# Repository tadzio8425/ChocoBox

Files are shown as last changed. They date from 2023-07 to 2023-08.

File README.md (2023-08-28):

<div>
  <h1>     ChocoBox</h1>
</div>

### Environment replicator for cocoa fermentation:
- Electronic system that replicates a real life environment. Includes:
  - Continous environmental humidity and temperature measurement
  - Real-time control of both humidity and temperature
  - Spline generation to emulate environmental changes
  - Intuitive set-up and data collection via .txt files
- Backend developed using the Arduino Framework and an ESP32 development board.
- Frontend mobile app developed using the Expo Framework and React-Native.
- Developed in the *Universidad de Los Andes* for the *Biomicrosystems research group*.

## Developed by: 
<ul>
  <li>Juan Sebastián Ortega (https://github.com/tadzio8425)</li>
  <li>Nicolás Correal (https://github.com/Correaln47)</li>
</ul>

## Quickstart
### 1. Setting-up the files...

#### i. Creating the files
The ChocoBox system uses three *.txt* files inside a **MicroSD Card** in order to function, these files are *environment.txt*, *spline.txt* and *datalog.txt*. Altough these files have the *.txt* format, their content is designed to be read as a *.csv*. For the proper functioning of the system, it is **obligatory** for the files to be named exactly like this. If it is your first time using ChocoBox, or if you are resetting the system, please delete all previous files from the SD Card and create three empty *.txt* files.

<p align="center">
   
</p>
<p align="center">
   <i>a. Contents of the MicroSD Card</i>
</p>

#### ii. Setting-up the environment
The environment to be replicated can be easily set in the *environment.txt* file. In order to to this, simply write the *csv* headers in the first row. These headers should be **hour, temperature, humidity**. Then, following the header order, write the desired values for specific hours in each new line. For example, this file replicates an environment for 96 hours, setting new desired values each 24 hours. There is no inverval restriction, neither there is a necessity for an interval, just make sure that the next hour is always greater than the previous one! **Please make sure that there are no extra new lines or blank spaces!**

<p align="center">
   
</p>
<p align="center">
   <i>b. Example of an environment.txt file</i>
</p>

#### iii. Joining the dots
In order to replicate how these variables behave smoothly in nature, a cubic spline algorithm is used in order to fill the gaps between the dots set in *environment.txt*. The results of this algorithm are saved by the microcontroller in *spline.txt*, so this file must not be modified in any way by the user. If the **reference values** shown by the system are not logical, please check the *spline.txt* file. A *spline.txt* with **Nan** values or other errors indicates that *environment.txt* was wrongly formated! 

<p align="center">
   
</p>
<p align="center">
   <i>c. Example of a correctly generated spline.txt file</i>
</p>

#### iv. Step by step
A fundamental part of the spline algorithm is the **step**, this value determines the interval for intermediate points to be calculated and also for data capture. For example, a step of **30 minutes** will make the system update its reference values and save its environmental data each, well, 30 minutes. The smaller the step, the more data will be captured and the smoother the system will be. **Beware of using extremely small steps, as they may lead to a memory overflow in the ESP32!** The **step can be modified by the user**, this will be explained in a further section.

#### v. Getting the data
All environmental data captured by the sensors is saved in *datalog.txt*, which is automatically updated by the microcontroller. This file includes the sensed information of each individual humidity and temperature sensor, captured each **step**. This file follows the order of the following headers: **time(min), tempA(degC), tempB(degC), tempC(degC), tempD(degC), humidLeft(%), humidRight(%)**

The presence of **Nan** values in this file may indicate a sensor malfunction!

<p align="center">
   
</p>
<p align="center">
   <i>d. Example of a correctly generated datalog.txt file</i>
</p>

## 2. PCB Connections
Handling the PCB should be avoided at all costs. However, in the case that something has gone wrong or a new interface/sensor needs to be added, the following connection diagram should be **strictly** followed. All cables are marked with their respective signal.

| PCB Overview |
| --- |
|   |

| DS18B20 (Temp) | DHT22 (Hum) | MicroSD |
| --- | --- | --- |
||||

| I2C (LCD Screen and Clock) | Humidifier and Heater Relay | 12V and WaterLevel |
| --- | --- | --- |
||||

## 3. Cable management
ChocoBox uses an electric extension to power itself, the extension input should be conected directly to the power socket. This extesion has 3 available output sockets, of which only 2 are actually used. One of the sockets must me connected to the **resistor cable**, which handles the power given to the heating resistors. The second socket must be connected to a **12V-2A** power supply that powers the electronics. The output of the power supply is a **jack connector** which goes directly into the PCB box. Remember that you may find the extension sockets on the floor, behind the resistor wooden holder. Please make sure that all major cables are correctly pluged-in before performing any test, also **do not handle cables under any circumstance unless the resistors are totally cold**.

- To completely **TURN-OFF** the system, you only need to unplug the extension input from the power socket.

## 4. Operating the system
Once everything is pluged-in, the system should start to work autonomously. This means that the desired values from *environment.txt* will be replicated inside the box, following the intermidiate points generated in *spline.txt* and the actual sensed values will be saved each **step** in *datalog.txt*.

### i. Monitoring 01: LCD Screen
The most straigth-forward method to monitor the system is by looking at its **20x4 LCD Screen**. This screen depicts the following data, line by line:
  1. **Humidity**: Displays the current humidity average inside the box in (%).
  2. **Temperature**: Displays the current temperature average inside the box in (°C).
  3. **Ref**: Displays the reference values that the system should be trying to achieve in that specific moment.
  4. **Time**: Displays how much time has the system been on a specific fermentation cycle. This timer **DOES NOT** reset when the system is disconnected, as it is programmed to retake fermentation despite a possible temporal failure. However, it can be reset **manually**.

| LCD Screen |
| --- |
|   |

### ii. Connecting to the ESP32 via WiFi
The ESP32 is set in *AP* mode, which means that it acts as an *Access Point* (A.K.A. its own WiFi network). In order to connect, simply search for the network called **ChocoBox** and establish a connection using the **secret password**. It is **important** that this password is only given to authorized staff, otherwise, a fermentation cycle could be jeopardized.

- **Once connected to the _ChocoBox_ network, the ESP32 can be accessed using its IP Address which will always be:**
- **192.168.1.1**

| The ChocoBox Network |
| --- |
|   |

### iii. Monitoring 02: Rest API

| Root: / |
| --- |
|   |

Accessing the root of the rest API via any browser (192.168.1.1/) displays the current state of its variables. Thus, ChocoBox can be monitored in real time without the need of an external app.

| Request | Path  | Description |
| --- | --- | --- |
| GET | /datalog  | Downloads the dataLog up to the latest measurement.|
| POST | /environment | Uploads an environment.txt to the system. When the system is reset, the uploaded file will set a new curve to follow. The included python script displays its POST format.|
| POST | /step | Updates the step of the spline algorithm. Its content must be a number that represents a certain number of hours (at least 0.05).|

### iv. Monitoring 03: App
An app was developed using the Expo Framework in order to unify all the API Requests in an intuitive and user friendly interface.

| Init Page| Main Page | Data Module |
| --- | --- | --- |
|  |  | |

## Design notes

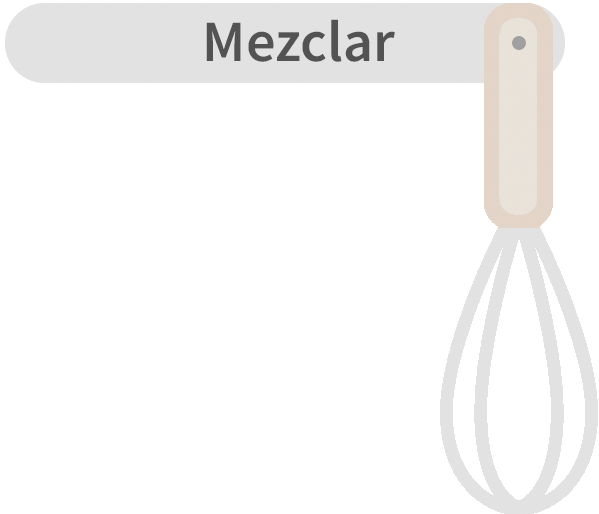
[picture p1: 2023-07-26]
ChocoboxApp/assets/images/batidora_mangotext.png

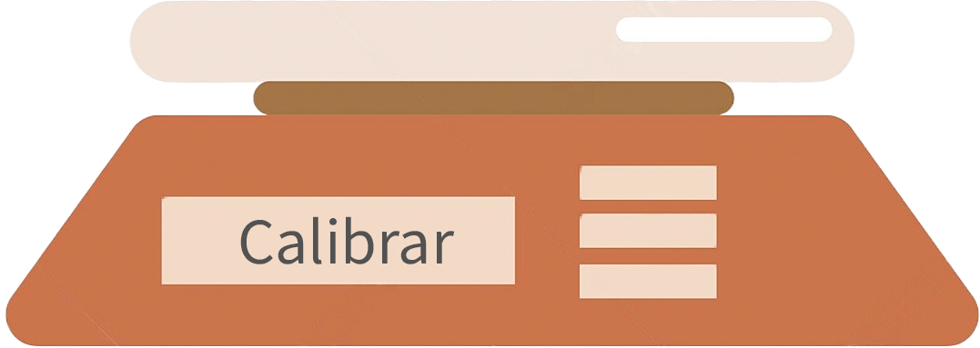
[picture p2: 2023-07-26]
ChocoboxApp/assets/images/balanza.png

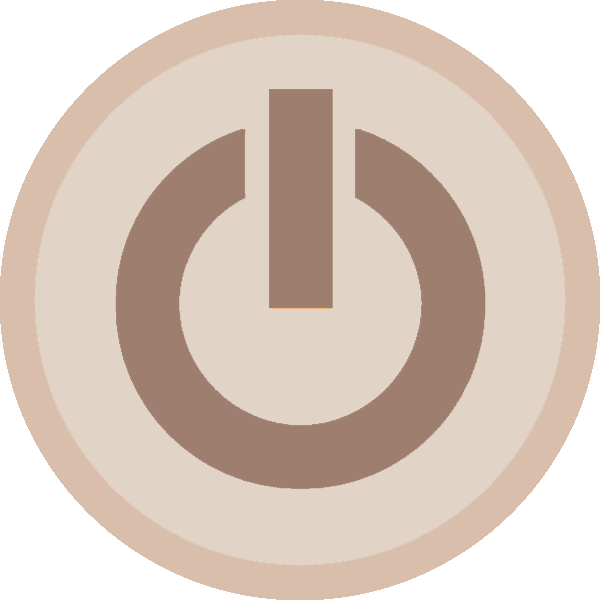
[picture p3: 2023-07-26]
ChocoboxApp/assets/images/offButton.png

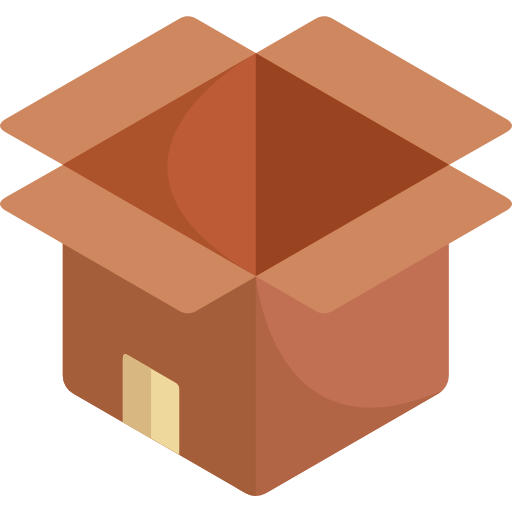
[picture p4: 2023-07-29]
ChocoboxApp/assets/images/package.png

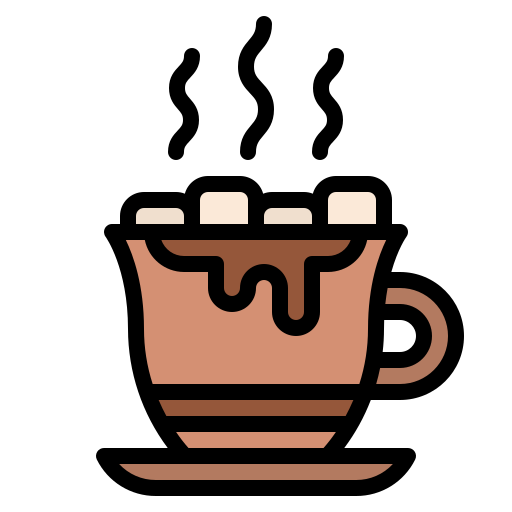
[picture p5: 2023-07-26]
ChocoboxApp/assets/images/hot-chocolate.png

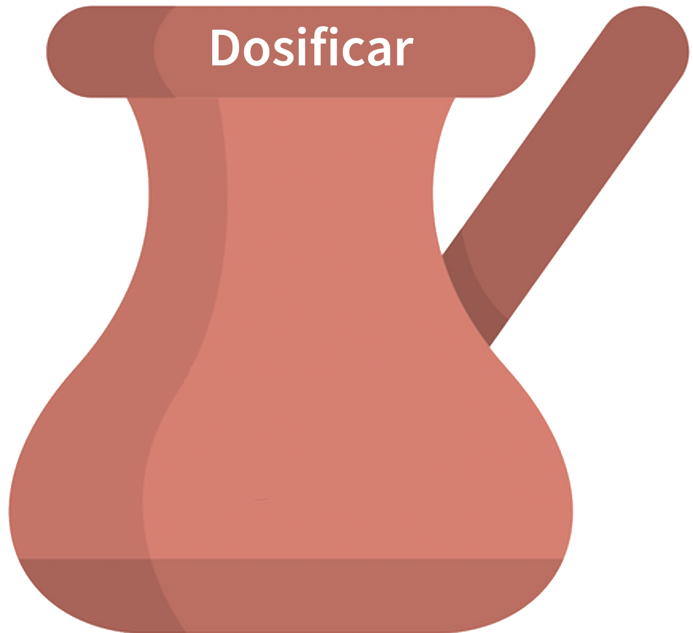
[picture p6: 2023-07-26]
ChocoboxApp/assets/images/chocolatera.png

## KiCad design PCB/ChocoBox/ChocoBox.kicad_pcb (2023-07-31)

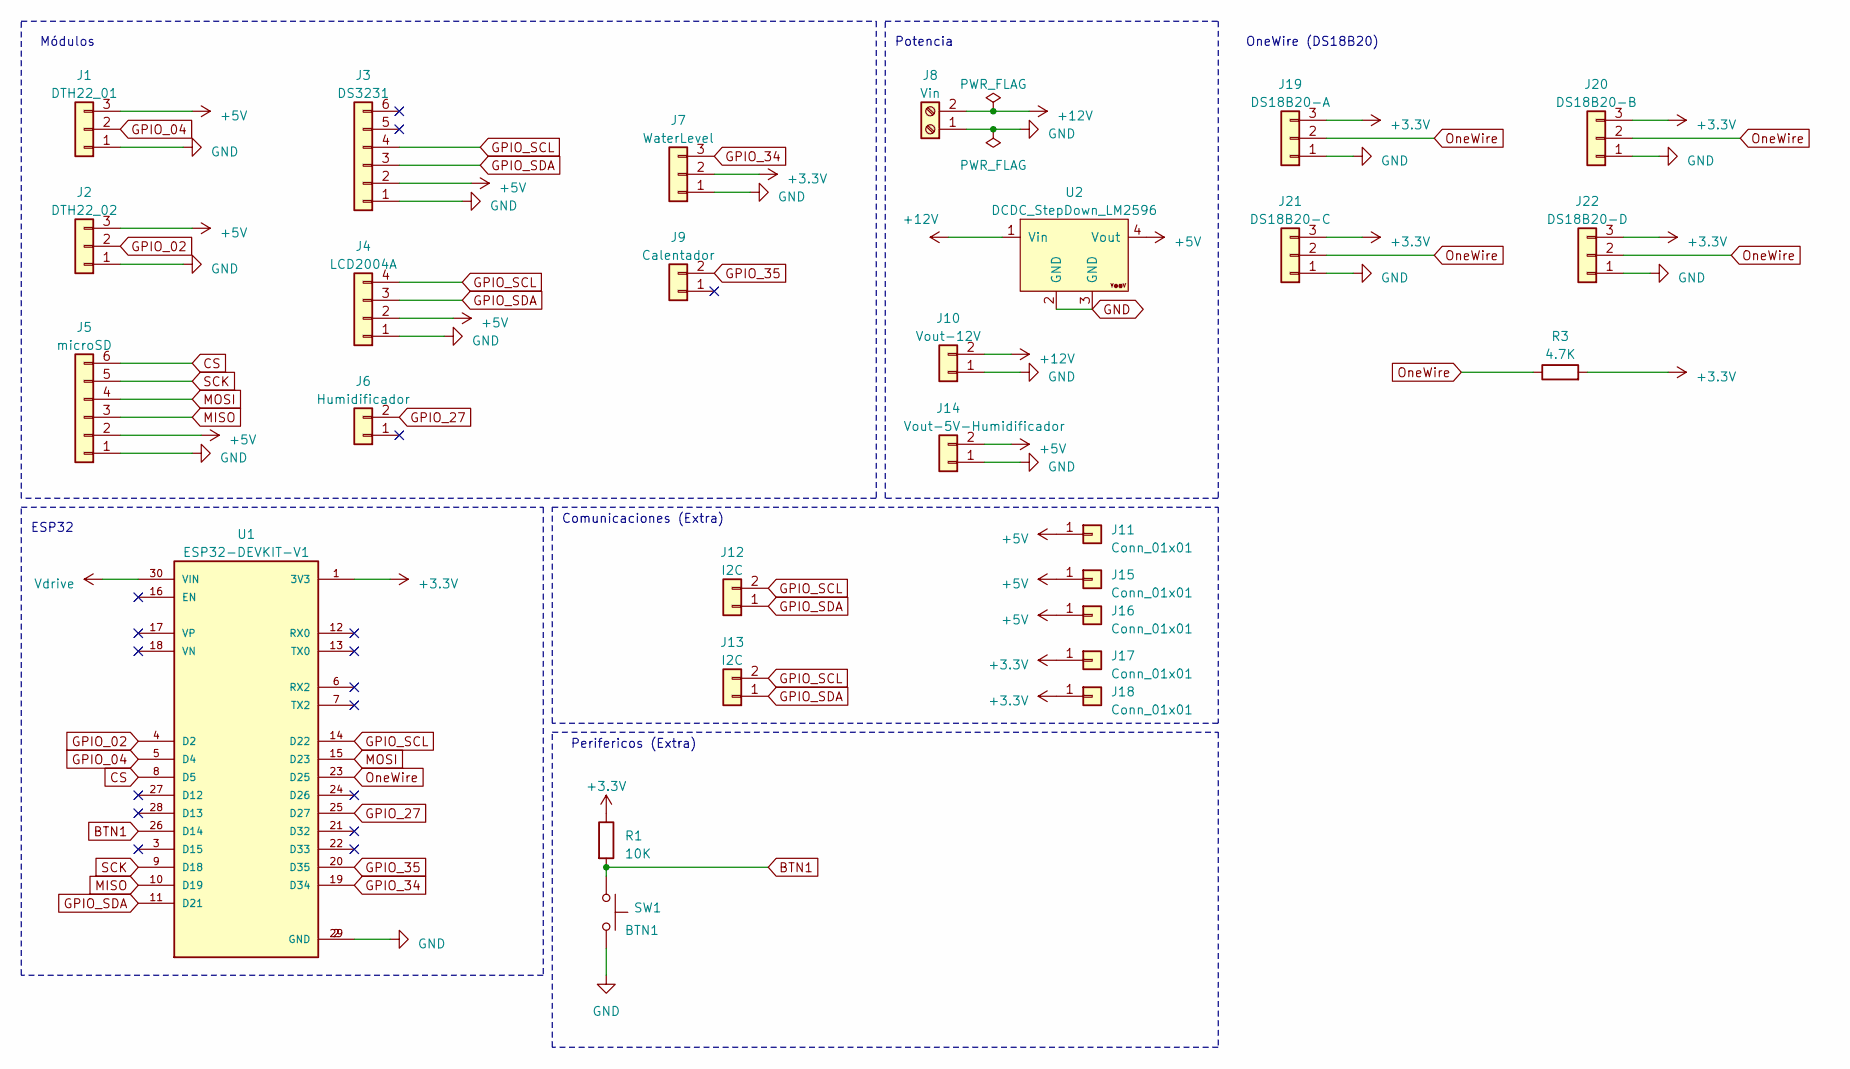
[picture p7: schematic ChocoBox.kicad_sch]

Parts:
J1: DTH22_01; PinSocket_1x03_P2.54mm_Vertical
J2: DTH22_02; PinSocket_1x03_P2.54mm_Vertical
J3: DS3231; PinSocket_1x06_P2.54mm_Vertical
J4: LCD2004A; PinSocket_1x04_P2.54mm_Vertical
J5: microSD; PinSocket_1x06_P2.54mm_Vertical
J6: Humidificador; PinSocket_1x02_P2.54mm_Vertical
J7: WaterLevel; PinSocket_1x03_P2.54mm_Vertical
J8: Vin; TerminalBlock_Phoenix_MKDS-1,5-2-5.08_1x02_P5.08mm_Horizont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
J9: Calentador; PinSocket_1x02_P2.54mm_Vertical
J10: Vout-12V; PinSocket_1x02_P2.54mm_Vertical
J11, J15, J16, J17, J18: Conn_01x01; PinSocket_1x01_P2.54mm_Vertical
J12, J13: I2C; PinSocket_1x02_P2.54mm_Vertical
J14: Vout-5V-Humidificador; PinSocket_1x02_P2.54mm_Vertical
J19: DS18B20-A; PinSocket_1x03_P2.54mm_Vertical
J20: DS18B20-B; PinSocket_1x03_P2.54mm_Vertical
J21: DS18B20-C; PinSocket_1x03_P2.54mm_Vertical
J22: DS18B20-D; PinSocket_1x03_P2.54mm_Vertical
R1: 10K; R_Axial_DIN0207_L6.3mm_D2.5mm_P10.16mm_Horizontal
R3: 4.7K; R_Axial_DIN0207_L6.3mm_D2.5mm_P10.16mm_Horizontal
SW1: BTN1; PinSocket_1x02_P2.54mm_Vertical
U1: ESP32-DEVKIT-V1; MODULE_ESP32_DEVKIT_V1; PARTREV N/A
U2: DCDC_StepDown_LM2596; YAAJ_DCDC_StepDown_LM2596

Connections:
+3.3V: J7.2, J17.1, J18.1, J19.3, J20.3, J21.3, J22.3, R1.1, R3.2, U1.1 (3V3)
+5V: J1.3, J2.3, J3.2, J4.2, J5.2, J11.1, J14.2, J15.1, J16.1, U2.4 (Vout)
+12V: J8.2, J10.2, U2.1 (Vin)
BTN1: R1.2, SW1.1, U1.26 (D14)
CS: J5.6, U1.8 (D5)
GND: J1.1, J2.1, J3.1, J4.1, J5.1, J7.1, J8.1, J10.1, J14.1, J19.1, J20.1, J21.1, J22.1, SW1.2, U1.2 (GND), U1.29 (GND), U2.2 (GND), U2.3 (GND)
GPIO_02: J2.2, U1.4 (D2)
GPIO_04: J1.2, U1.5 (D4)
GPIO_27: J6.2, U1.25 (D27)
GPIO_34: J7.3, U1.19 (D34)
GPIO_35: J9.2, U1.20 (D35)
GPIO_SCL: J3.4, J4.4, J12.2, J13.2, U1.14 (D22)
GPIO_SDA: J3.3, J4.3, J12.1, J13.1, U1.11 (D21)
MISO: J5.3, U1.10 (D19)
MOSI: J5.4, U1.15 (D23)
OneWire: J19.2, J20.2, J21.2, J22.2, R3.1, U1.23 (D25)
SCK: J5.5, U1.9 (D18)
Vdrive: U1.30 (VIN)

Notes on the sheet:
Módulos
OneWire (DS18B20)
ESP32
Perifericos (Extra)
Comunicaciones (Extra)
Potencia

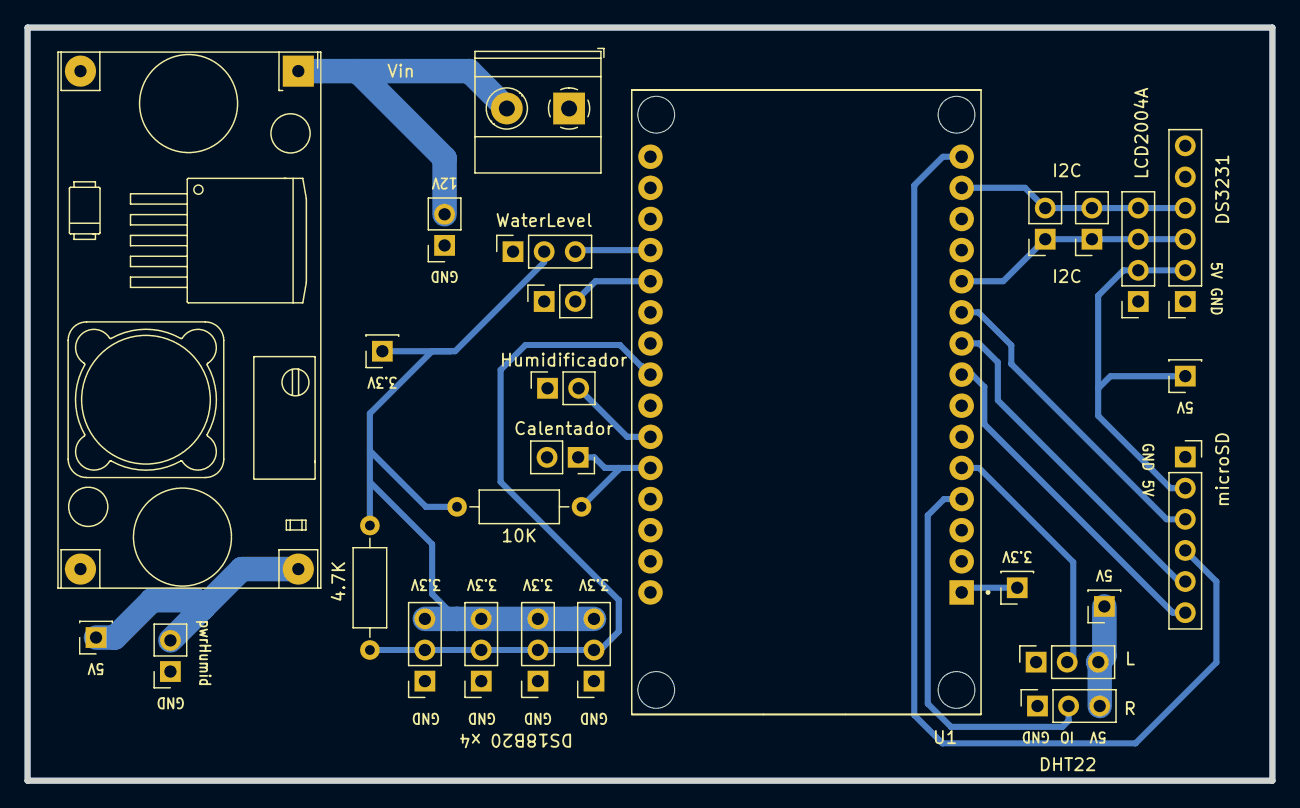
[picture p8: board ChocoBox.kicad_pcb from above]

Board: 2 copper layers, 101.6 x 61.5 mm, 27 parts (0 on the bottom side), 17 nets.

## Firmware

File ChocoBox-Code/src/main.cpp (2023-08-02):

#include <Arduino.h>
#include <ConnecT.h>
#include <Humidifier.h>
#include "DHT.h"
#include "HumidityController.h"
#include "RTClib.h"
#include <Adafruit_Sensor.h>
#include <Wire.h> 
#include <LiquidCrystal_I2C.h>
#include <TemperatureController.h>
#include <Heater.h>
#include <Interpol.h>
#include "SPIFFS.h"
#include <Preferences.h>
#include <ChocoBoxREST.h>
#include <SD.h>
#include <Adafruit_GFX.h>
#include <SPI.h>
#include <OneWire.h>
#include <DallasTemperature.h>
#include <MovingAverage.h>


using namespace ChocoBoxREST;

std::vector<float> x;
std::vector<float> v_temp;
std::vector<float> v_humidity;
std::vector<float> xq;

std::vector<float> vq_temp;
std::vector<float> vq_humidity;

const int numOfHours = 336; // Número de horas que dura la fermentación
float paso = 0.5; // Paso de la interpolación - Se cambia la temperatura y la humedad cada {paso} horas - Default cada media hora
const int buffer_size = numOfHours/paso;

//Archivos tarjeta SD
File dataFile;
File environmentFile;
File splineFile;

File dataFileApp;


/* Funciones de ayuda */
void printVector(const std::vector<float>& vec) {
    for (float value : vec) {
        Serial.print(value, 3);
        Serial.print(",");
    }
    Serial.println();
}


void extractEnvironmentData(const String& data, std::vector<float>& hourVec,
                 std::vector<float>& temperatureVec, std::vector<float>& humidityVec) {


    int lineCount = 0;

    int startIndex = 0;
    int endIndex = data.indexOf('\n');
    bool isFirstLine = true;   // Flag to skip the first line
    bool isSecondLine = true;  // Flag to skip the second line
    while (endIndex != -1) {
        String line = data.substring(startIndex, endIndex);
        int commaIndex1 = line.indexOf(',');
        int commaIndex2 = line.indexOf(',', commaIndex1 + 1);
        if (!isFirstLine && !isSecondLine && commaIndex1 != -1 && commaIndex2 != -1) {
            float hour = line.substring(0, commaIndex1).toFloat();
            float temperature = line.substring(commaIndex1 + 1, commaIndex2).toFloat();
            float humidity = line.substring(commaIndex2 + 1).toFloat();
            hourVec.push_back(hour);
            temperatureVec.push_back(temperature);
            humidityVec.push_back(humidity);
        }

        lineCount++;

        isFirstLine = false;

        if(lineCount == 2){
          isSecondLine = false;
        }

        startIndex = endIndex + 1;
        endIndex = data.indexOf('\n', startIndex);
        if (endIndex == -1 && startIndex < data.length()) {
            // Handle the last line if it doesn't end with a newline character
            endIndex = data.length();
        }
    }
}



void sendSplineSD(const std::vector<float>& hourVec,
                          const std::vector<float>& temperatureVec,
                          const std::vector<float>& humidityVec) {
    String dataString;
    for (size_t i = 0; i < hourVec.size(); ++i) {
        dataString += String(hourVec[i], 3) + "," + String(temperatureVec[i], 3) + "," +
                      String(humidityVec[i], 3) + "\n";
    }

    splineFile = SD.open("/spline.txt", FILE_WRITE);
    splineFile.print(dataString);
    splineFile.flush();
    splineFile.close();
}



/* Pines */
#define PIN_HUM 27 // Pin del Humidificador
#define PIN_HEAT 14 // Pin del Calentador

#define DHTTYPE DHT22  // DHT 22  (AM2302), AM2321 - SDA: 21, SCL: 22
#define DHTPIN_01 4 // Pin del sensor DHT 01
#define DHTPIN_02 2 // Pin del sensor DHT 02

#define ONE_WIRE_BUS 25 //Pin OneWire

#define chipSelect 5 //Pin de CS

#define PIN_WTR 34 //Pin análogo para el sensor de nivel de agua


//Direcciones DS18B20
uint8_t sensA_add[] = {0x28, 0xFF, 0x64, 0x1E, 0XF6, 0x66, 0x6D, 0x5F};
uint8_t sensB_add[] = {0x28, 0xFF, 0x64, 0x1E, 0xF7, 0x84, 0x80, 0x04};
uint8_t sensC_add[] = {0x28, 0xFF, 0x64, 0x1E, 0xF7, 0x96, 0x3D, 0xB6};
uint8_t sensD_add[] = {0x28, 0xFF, 0x64, 0x1E, 0x1F, 0x84, 0x68, 0xCD};



//IMPORTANTE - VARIABLE QUE HABILITA EL WIFI
bool useWiFi = false;

/* Sensores -  Variables */
int waterLevel = 0; //Variable que almacena el nivel de agua
float humidity_01 = 0; // Variable que almacena la humedad
float temperature_01 = 0; // Variable que almacena la temperatura
float humidity_02 = 0; // Variable que almacena la humedad
float temperature_02 = 0; // Variable que almacena la temperatura
uint32_t ferm_time = 0; // Variable que almacena el tiempo de fermentación
float ferm_time_hr = 0; // Variable que almacena el tiempo de fermentación en horas
uint32_t prev_ferm_time = 0; // Variable que almacena el tiempo de fermentación previo
int prev_index = -1; // Variable que almacena el índice previo de la interpolación

float ds18b20_A = 0;
float ds18b20_B = 0;
float ds18b20_C = 0;
float ds18b20_D = 0;

double global_temp = 0;
float global_humidity = 0;

/* Variables de control */
float desiredHumidity = 0; // Variable que almacena la humedad deseada
double desiredTemperature = 0; // Variable que almacena la temperatura deseada
uint32_t now = 0; // Variable que almacena el tiempo actual
bool* resetPointer;
bool defaultReset = false; 
bool wifiAtSetup = true;
float timer_start = 0;

/* Control del log - Persistencia de los datos */
int log_interval = (60*1000) * 30; // Intervalo de tiempo entre cada registro en la base de datos (en milisegundos)
long log_persistence = (24*60*60) * 30; // Tiempo de persistencia de los datos en la base de datos (en segundos) 


/* Objetos */
ConnecT connecT; // Instancia de la clase ConnecT: Permite la cone1pasoxión a internet y la comunicación con el servidor web
Humidifier humidifier; // Instancia de la clase Humidifier: Permite el control del humidificador
Heater heater; // Instancia de la clase Heater: Permite el control del calentador
DHT dht_01(DHTPIN_01, DHTTYPE); // Instancia de la clase DHT: Permite la lectura de los sensores DHT
DHT dht_02(DHTPIN_02, DHTTYPE); // Instancia de la clase DHT: Permite la lectura de los sensores DHT
HumidityController humidityController(&global_humidity, &humidifier); // Instancia de la clase HumidityController: Permite el control de la humedad
TemperatureController temperatureController(&desiredTemperature, &global_temp, &heater); // Instancia de la clase TemperatureController: Permite el control de la temperatura
RTC_DS3231 rtc; // Instancia de la clase RTC_DS3231: Permite la lectura del RTC
LiquidCrystal_I2C lcd(0x27, 20, 4); // Instancia de la clase LiquidCrystal_I2C: Permite la comunicación con la pantalla LCD
Interpol interpol; // Instancia de la clase Interpol: Permite la interpolación de los datos
Preferences preferences; // Instancia de la clase Preferences: Permite el almacenamiento de datos en la memoria flash
OneWire oneWire(ONE_WIRE_BUS); //Instancia de la clase OneWire, permite conectarse a los dispositivos que usen este protocolo
DallasTemperature tempSensors(&oneWire); //Instancia de DallasTemperature para los DS18B20
MovingAverage* tempAverage = new MovingAverage(); //Objeto que almacenará el promedio de las temperaturas
MovingAverage* humidAverage = new MovingAverage();

char dateBuff[20];


/* Funciones */

void updateEnvironment(){

  String environment_str;

  environmentFile = SD.open("/environment.txt");
  if (environmentFile) {
    while (environmentFile.available()) {
    	environment_str = environmentFile.readString();
    }
    // close the file:
    environmentFile.close();
  } else {
    Serial.println("Error abriendo environment.txt");
  }

  //Se actualizan los vectores de la interpolación
  extractEnvironmentData(environment_str, x, v_temp, v_humidity);

  xq = interpol.generateXq(x[0], x[x.size()-1], paso);

  vq_temp = interpol.cubicSpline(x, v_temp, xq);
  vq_humidity = interpol.cubicSpline(x, v_humidity, xq);

  /*Subir a la tarjeta SD el resultado (vq_temp y vq_humidity)*/
  sendSplineSD(xq, vq_temp, vq_humidity);

  x.clear();
  v_temp.clear();
  v_humidity.clear();
  xq.clear();
  vq_temp.clear();
  vq_humidity.clear();
}

//Download a file from the SD, it is called in void SD_dir()
void downloadDataLog()
{
  {
    File download = SD.open("/datalog.txt");
    if (download) 
      {
        (connecT.getServerPointer()) -> sendHeader("Content-Type", "text/text");
        (connecT.getServerPointer()) -> sendHeader("Content-Disposition", "attachment; filename=datalog.txt");
        (connecT.getServerPointer()) -> sendHeader("Connection", "close");
        (connecT.getServerPointer()) -> streamFile(download, "application/octet-stream");
        download.close();
      } else Serial.println("Error sending a file!"); 
  }

}


//Handles the file upload a file to the SD
File UploadFile;
//Upload a new file to the Filing system
void handleFileUpload()
{ 
  HTTPUpload& uploadfile = (connecT.getServerPointer()) -> upload(); //See https://github.com/esp8266/Arduino/tree/master/libraries/ESP8266WebServer/srcv
                                            //For further information on 'status' structure, there are other reasons such as a failed transfer that could be used
  if(uploadfile.status == UPLOAD_FILE_START)
  {
    String filename = uploadfile.filename;
    if(!filename.startsWith("/")) filename = "/"+filename;
    Serial.print("Upload File Name: "); Serial.println(filename);
    SD.remove(filename);                         //Remove a previous version, otherwise data is appended the file again
    UploadFile = SD.open(filename, FILE_WRITE);  //Open the file for writing in SD (create it, if doesn't exist)
    filename = String();
  }
  else if (uploadfile.status == UPLOAD_FILE_WRITE)
  {
    if(UploadFile) UploadFile.write(uploadfile.buf, uploadfile.currentSize); // Write the received bytes to the file
  } 
  else if (uploadfile.status == UPLOAD_FILE_END)
  {
    if(UploadFile)          //If the file was successfully created
    {                                    
      UploadFile.close();   //Close the file again
      Serial.print("Upload Size: "); Serial.println(uploadfile.totalSize);
      (connecT.getServerPointer()) -> send(200,"text/html", "File uploaded!");
    } 
    else
    {
      (connecT.getServerPointer()) -> send(501,"text/html", "Error!");
    }
  }
}
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

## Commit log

2023-06-06 Sensorica en tiempo real
2023-06-06 Sensores DHT medidos
2023-06-06 Controlador Temperatura
2023-06-07 Problemas de memoria arreglados
2023-06-08 Avance PCB y pines
    [ChocoBox.kicad_pcb, ChocoBox.kicad_sch]
2023-06-08 Inicio PCB
    [ChocoBox.kicad_pcb, ChocoBox.kicad_sch]
2023-06-26 PCB V1 Terminada
    [ChocoBox.kicad_pcb, ChocoBox.kicad_sch]
2023-06-27 PCB terminada
    [ChocoBox.kicad_pcb, ChocoBox.kicad_sch]
2023-07-08 Controladores funcionando
    [ChocoBox-Edge_Cuts.gbr, ChocoBox-F_Cu.gbr, ChocoBox-F_Mask.gbr, ChocoBox-F_Paste.gbr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]
2023-07-13 Prueba con resistencia y moving average
2023-07-13 Prueba resistencia
2023-07-22 Temperatura funcionando
2023-07-27 subir y descargar desde la app
2023-07-29 Cambio de logo app
2023-07-31 Bug fix - App environment.txt
    [ChocoBox.kicad_pcb]
2023-08-02 Cambio step en la app
2023-08-02 Barra nivel de agua en app
